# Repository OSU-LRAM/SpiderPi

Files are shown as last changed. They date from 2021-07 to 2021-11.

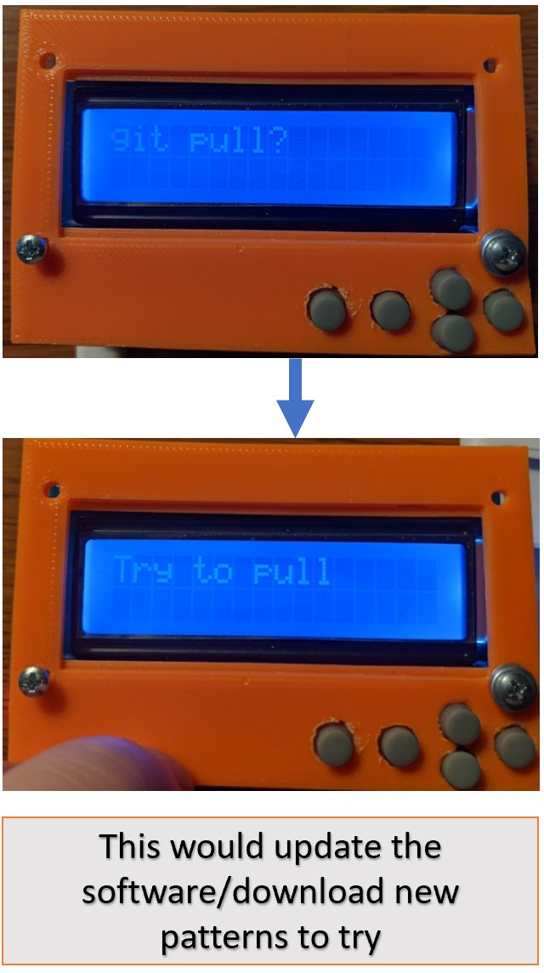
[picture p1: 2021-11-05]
Build Resources/Photos/GUI_2.jpg

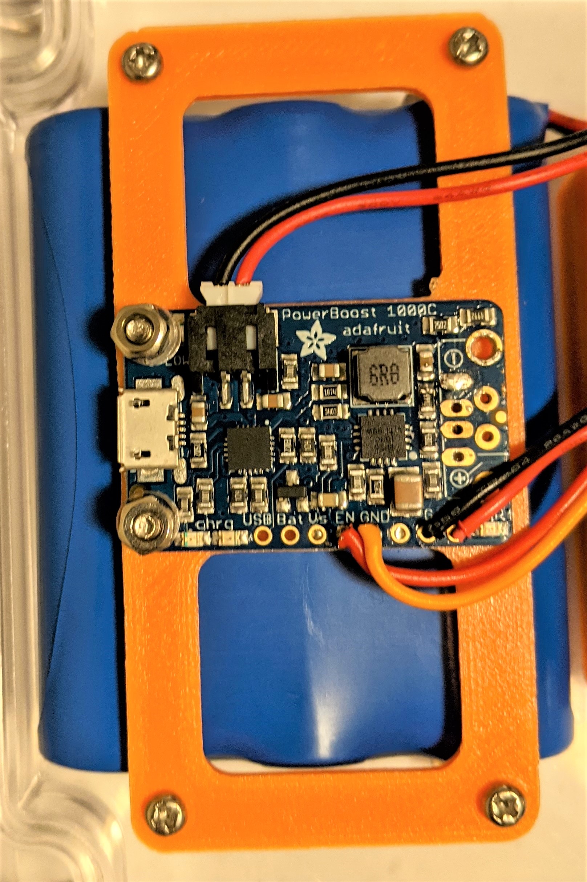
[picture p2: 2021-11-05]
Build Resources/Photos/PXL_20210928_055308199.MP.jpg

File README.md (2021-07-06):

# SpiderPi
Raspberry Pi Repo for generating and playing .wav files to actuate spider webs with ear buds.

Resources For Setting Up SpiderPi

Build Adafruit LCD Plate/Keypad and setup code
https://learn.adafruit.com/adafruit-16x2-character-lcd-plus-keypad-for-raspberry-pi

Install Pygame on Raspberry Pi:
python3 -m pip install pygame==2.0.0
sudo apt-get install git curl libsdl2-mixer-2.0-0 libsdl2-image-2.0-0 libsdl2-2.0-0 libsdl2-ttf-2.0-0
https://www.raspberrypi.org/forums/viewtopic.php?t=291180

Setup launch Script using crontab:
https://www.instructables.com/Raspberry-Pi-Launch-Python-script-on-startup/

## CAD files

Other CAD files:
Build Resources/RaspberryPi Case/Battery_Plate.ipt
Build Resources/RaspberryPi Case/Button_Pin.ipt
Build Resources/RaspberryPi Case/Button_Plate.ipt
Build Resources/RaspberryPi Case/OldVersions/Button_Pin.0002.ipt
Build Resources/RaspberryPi Case/OldVersions/Button_Plate.0004.ipt

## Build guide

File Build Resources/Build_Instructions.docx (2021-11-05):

# Making the SpiderPi

# Setting up the Raspberry pi

Flash a headless raspberry pi image onto micro sd card (at least 8GB, I used 32GB) using raspberry pi imager software or equivalent. There’s lots of tutorials online on how to do this.

Unplug and replug micro sd card into computer. Add a blank <ssh> file to boot to enable ssh.

Plug pi into ethernet and ssh to raspberrypi using <ssh pi@raspberrypi.local> It will then ask for a password, which is set to <raspberry> as a default. Then use <sudo raspi-config> to open the pi settings. Here you can add the necessary Wi-Fi information.

If not able to use ethernet, edit wpa_supplicant.conf file while adding ssh file to boot to add Wi-Fi information directly. This must be done before powering the raspberry pi the first time with the micro sd card. https://raspberrypihq.com/how-to-connect-your-raspberry-pi-to-wifi/ or https://www.raspberrypi.org/documentation/computers/configuration.html. I found this method to be prone to errors. Use ethernet if possible.

# Building the LCD Screen w/buttons

Follow instructions at https://learn.adafruit.com/adafruit-16x2-character-lcd-plus-keypad-for-raspberry-pi. This website also has instructions on how to set up the software to use the Adafruit LCD screen.

# Setting up the software

Install Pygame Library

- python3 -m pip install pygame==2.0.0
- sudo apt-get install git curl libsdl2-mixer-2.0-0 libsdl2-image-2.0-0 libsdl2-2.0-0 libsdl2-ttf-2.0-0
- https://www.raspberrypi.org/forums/viewtopic.php?t=291180

Install GitPython Library

- https://gitpython.readthedocs.io/en/stable/intro.html
- This process may need debugging, I don’t remember if I used something else (update).

Clone GitHub repo to SpiderPi

- https://github.com/OSU-LRAM/SpiderPi

Setup launch Script using crontab to start GUI when SpiderPi is powered:

- https://www.instructables.com/Raspberry-Pi-Launch-Python-script-on-startup/

# Parts List

## Electronics Needed to Function

- 1 Raspberry Pi (4 B)
- 1 Micro SD Card

https://www.amazon.com/Silicon-Power-Speed-MicroSD-Adapter/dp/B07Q384TPK?tag=georiot-us-default-20&ascsubtag=tomshardware-us-6454569509847805000-20&geniuslink=true

- 1 X LCD + keypad Kit for Raspberry Pi from Adafruit

https://www.amazon.com/Adafruit-White-Keypad-Raspberry-ADA1115/dp/B00N973FZI/ref=sr_1_1?dchild=1&keywords=Adafruit+LCD%2BKeypad+Kit&qid=1621909463&sr=8-1

- 1 x stacking header for pin access (header was too short in the kit from Adafruit)

https://www.adafruit.com/product/1112

- cheap earbuds with large speaker radius
- extra wiring
- 1 X Audio Amplifier Chip https://www.amazon.com/HiLetgo%C2%AE-PAM8403-Digital-Amplifier-2-5-5V/dp/B00LODGV64/ref=asc_df_B00LODGV64/?tag=hyprod-20&linkCode=df0&hvadid=312154678244&hvpos=&hvnetw=g&hvrand=5191437459944121002&hvpone=&hvptwo=&hvqmt=&hvdev=c&hvdvcmdl=&hvlocint=&hvlocphy=9027836&hvtargid=pla-634475605665&psc=1

## Case Components

- 1X waterproof case

https://sixfab.com/product/raspberry-pi-ip54-outdoor-iot-project-enclosure/

- 1X set of silicone rubber push button covers

https://www.ebay.com/itm/224145008728?chn=ps&norover=1&mkevt=1&mkrid=711-117182-37290-0&mkcid=2&itemid=224145008728&targetid=1288994547794&device=c&mktype=pla&googleloc=1024429&poi=&campaignid=11613469917&mkgroupid=117473130610&rlsatarget=pla-1288994547794&abcId=9300455&merchantid=8233684&gclid=CjwKCAjw-qeFBhAsEiwA2G7Nl8LDyeOwPTJKYqnbdavzQloUIuyVgsUNL7y5E-2T5mca_JcrWwzH8hoCDx4QAvD_BwE

- 1 X set of standoff fasteners

https://www.amazon.com/iUniker-Raspberry-Installation-Standoff-Accessories/dp/B096ZMN8W7/ref=sr_1_1_sspa?dchild=1&keywords=raspberry+pi+standoff&qid=1626194642&s=electronics&sr=1-1-spons&psc=1&spLa=ZW5jcnlwdGVkUXVhbGlmaWVyPUFJTTJaM1gzMUIwSTImZW5jcnlwdGVkSWQ9QTA1MjUxMjIyVzlHU0FKM0JDVkxCJmVuY3J5cHRlZEFkSWQ9QTAyMzc2NDIyQklCUDE5SzAxUDMmd2lkZ2V0TmFtZT1zcF9hdGYmYWN0aW9uPWNsaWNrUmVkaXJlY3QmZG9Ob3RMb2dDbGljaz10cnVl

- 1 X Lipo Battery
- https://www.adafruit.com/product/353
- 1 X battery charger chip

https://www.adafruit.com/product/2465

- 1 X battery charger cable

https://www.adafruit.com/product/1995

- 1 X waterproof power switch

https://www.amazon.com/TWTADE-Waterproof-Momentary-Stainless-YJ-GQ16BH-M-W/dp/B07YKV9M8M/ref=sr_1_2?dchild=1&keywords=waterproof%2Billuminated%2Bbutton&qid=1627409880&s=industrial&sr=1-2&th=1

- 1 X 3d printed lcd base
- 5 X 3d printed pushbutton pins
- 1 X 3d printed battery base

# Case Assembly

Use 3d printed lcd base and 3d printed battery base as guides on where to drill holes through the case lid. The button holes need to be countersunk on the inside to make room for the silicone pushbuttons. The outer ring of the buttons was glued into the countersunk holes. Once the holes have been drilled and the silicone buttons glued in, the LCD screen board can be screwed on. The standoff fasteners will bridge the gap between the board and the board base.

The battery charging chip mounts to the underside of the battery on the 3d printed battery base. The chip must be mounted to the printed base before the battery and base are screwed to the lid.

## Wiring the charging chip to the pi and the power switch

The battery chip’s GND and EN pins need to be wired to the power switch’s NC and C pins, respectively. The G and 5V pins need to be wired to the Ground and 5V Power pins on the Raspberry Pi, respectively.

The pushbutton switch also needs 5V and Ground from the Raspberry Pi to its + and – pins respectively. The 5v to + pin needs a resistor between the two, just like a typical led would. 1K ohms works fine.

The Audio Amplifier chip also needs 5V and ground from the Raspberry Pi to its 5V + and – pins. The Audio Amplifier chip needs the + and minus of one side of the Audio jack to connect to its L and Ground pins. Finally, the Speaker pins need to connect to the + and – from the Amplifier chip.

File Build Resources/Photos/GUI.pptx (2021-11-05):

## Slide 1

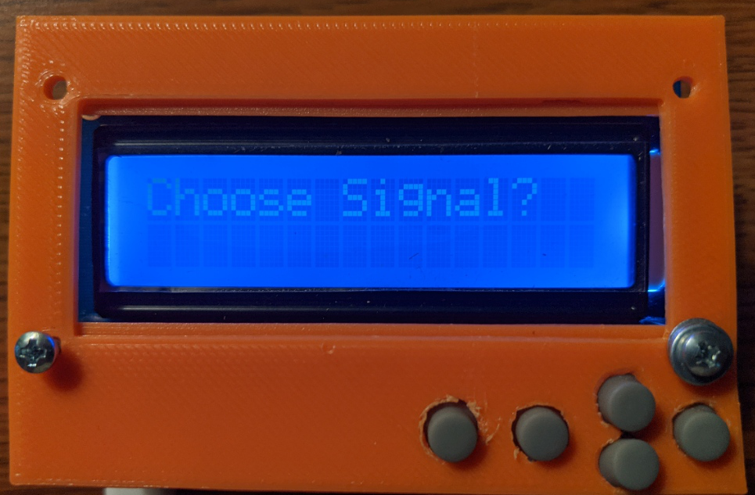
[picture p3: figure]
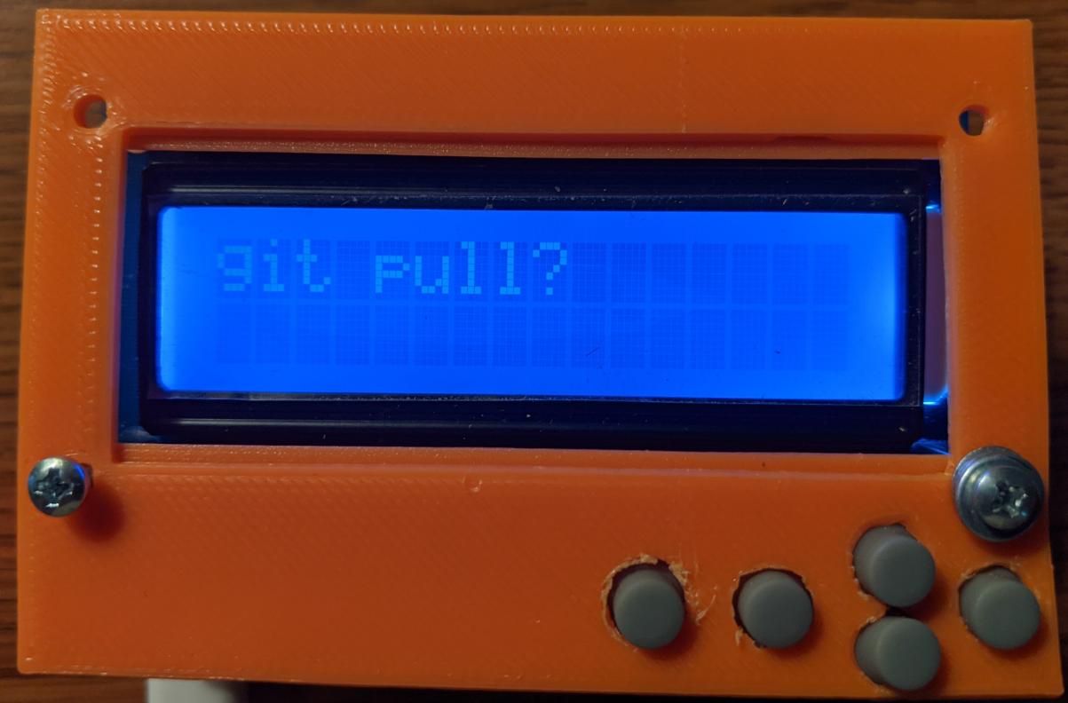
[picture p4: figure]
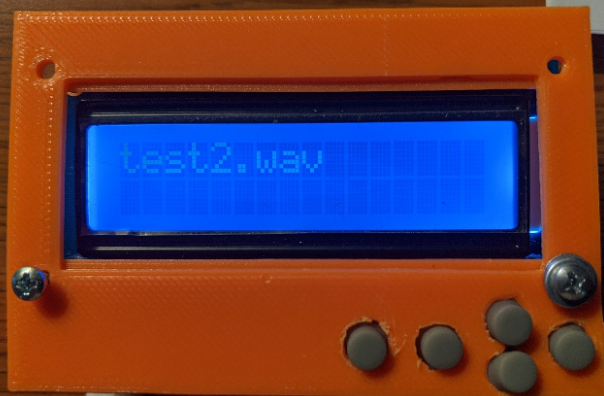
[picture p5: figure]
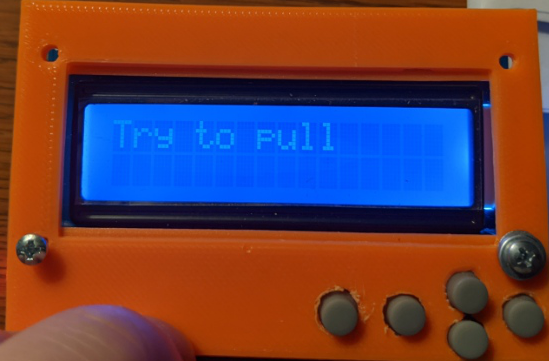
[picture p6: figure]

This would update the software/download new patterns to try

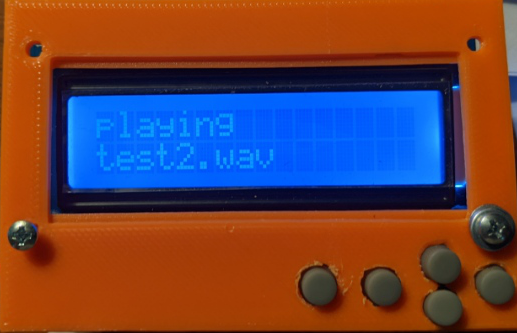
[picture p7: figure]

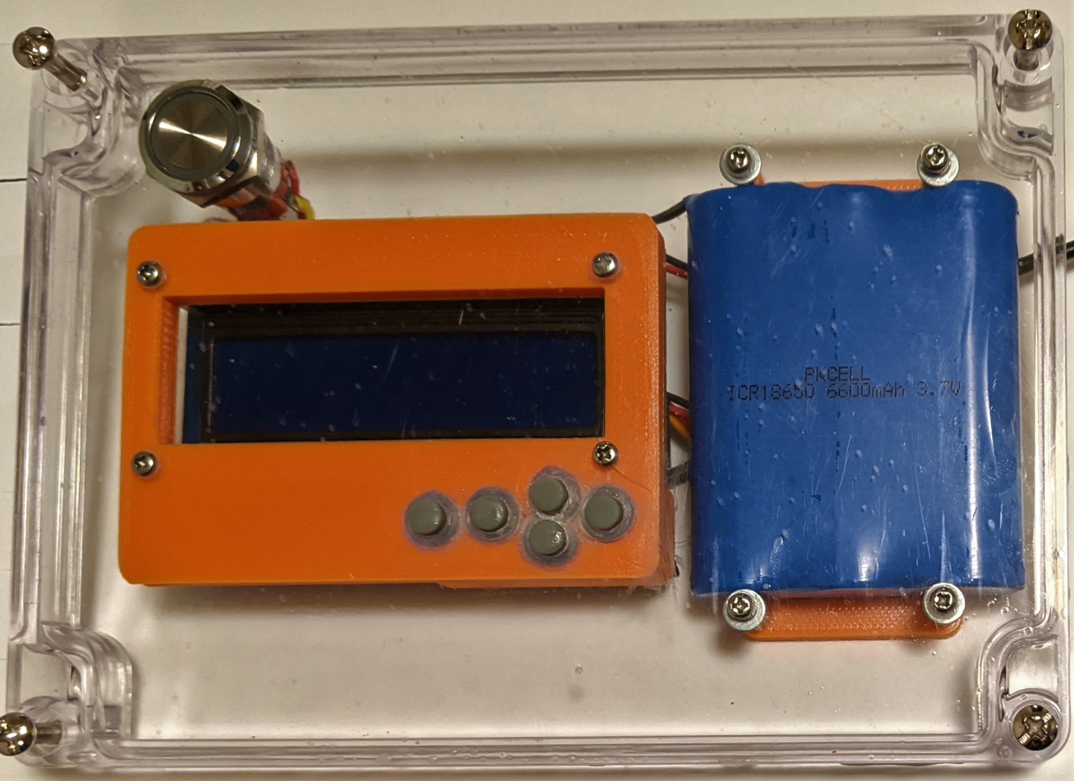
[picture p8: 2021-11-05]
Build Resources/Photos/PXL_20210928_055515309.MP.jpg

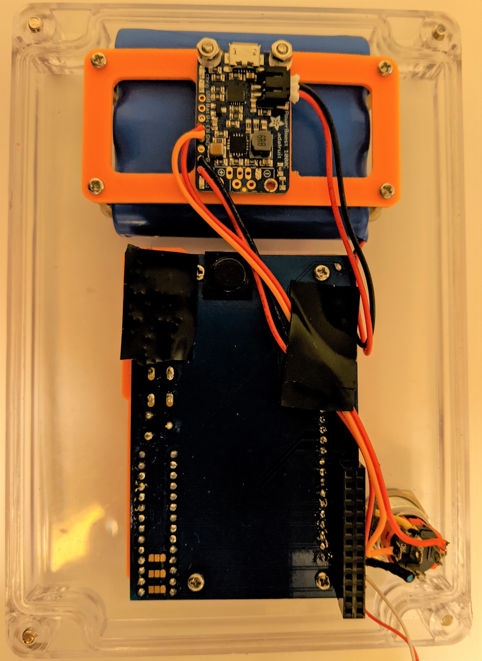
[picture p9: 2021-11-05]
Build Resources/Photos/PXL_20210928_055322346.MP.jpg

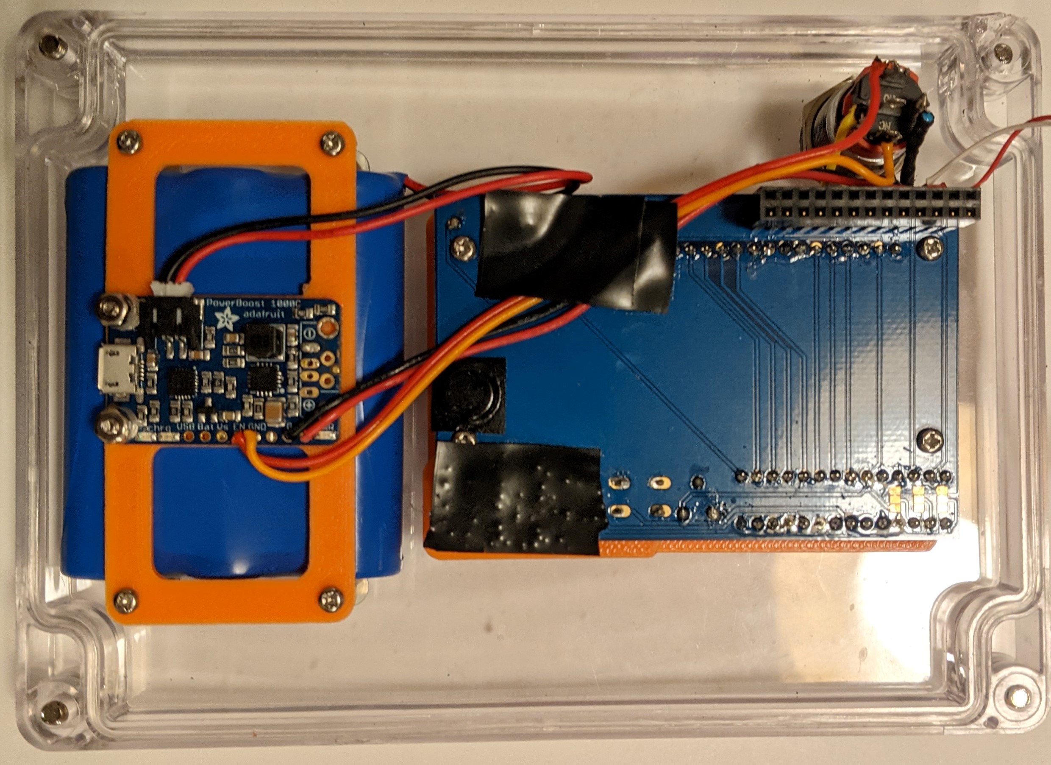
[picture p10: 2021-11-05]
Build Resources/Photos/PXL_20210928_055256160.MP.jpg

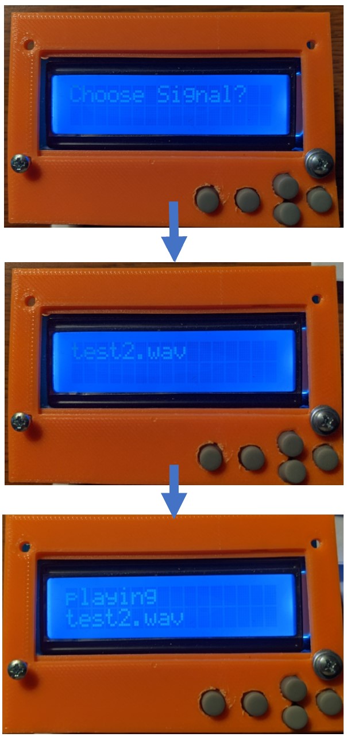
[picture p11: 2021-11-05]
Build Resources/Photos/GUI_1.jpg

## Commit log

2021-07-06 Cleaning up printing
2021-08-03 more printing
2021-11-05 Adding resources for building the spider pi
    [Battery_Plate.ipt, Button_Pin.0002.ipt, Button_Pin.ipt, Button_Plate.0004.ipt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]
